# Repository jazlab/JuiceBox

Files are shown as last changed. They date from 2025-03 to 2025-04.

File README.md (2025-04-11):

# :beverage_box:JuiceBox: a liquid reward delivery system

JuiceBox is a liquid reward delivery system designed for animal training and experiments. The system consists of:

1. A control box, which:
    - allows for valve control via computer (auto) and manual inputs,
    - features timed-draining for safe and convenient cleaning, and
    - includes mounting holes for the valve and a tube holder.
2. A bottle holder, which:
    - securely holds the juice bottle in place,
    - allows for quick and easy bottle removal, and
    - includes a tube holder to keep your hands free.

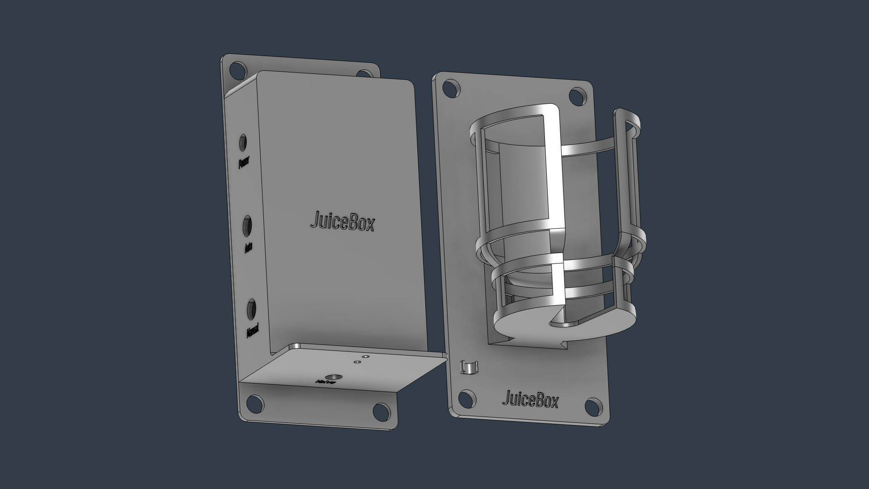
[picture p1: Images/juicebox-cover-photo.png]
Cover photo


## Table of Contents
- [Building & setting up your own JuiceBox](#building--setting-up-your-own-juicebox)
- [Using JuiceBox](#using-juicebox)
- [Circuit diagram](#circuit-diagram)
- [Latency test](#latency-test)
- [Contact](#contact)

## Building & setting up your own JuiceBox

### 0. Gather tools and supplies

The table below lists all the tools and supplies you’ll need to build a JuiceBox from scratch. If you already have a functioning control box, you’ll only need a 24V DC power cable, things listed in “Juice Bottle & Holder” and “Mounting,” and any relevant tools.

|  | **Name** | **Qty** | **Purpose & Specifications** |
| --- | --- | --- | --- |
| **Circuit Board** | PCB board | 1 | Custom files provided in this repository. See ordering instructions below. |
|  | 7805 voltage regulator | 1 | Can be pre-assembled on the PCB board (see PCB ordering instruction below). [Example product](https://www.amazon.com/ALLECIN-L7805-Regulator-Positive-Regulators/dp/B0CBKCDT4H/ref=sr_1_4?crid=2WCJKAQUHKRN7&dib=eyJ2IjoiMSJ9.yJzEi34CZ1WRm1_J6qxU1pyW9wghQLtg6IbF4fboZbTi889ok1h4hG9QhPJFAEpCzUIHdzyGpYp6OKTvsvIaCrYhlPovNcXIZuAi9Dkfmnm6QhzktdkW-ZoMuQcdPGAh4T31KEgbjpQAathV_9ffThyl1RSwhNaUL8IgItWbd8ZooAMghe03Zn5gxsPbM6_Zx74NqrIcUzpZuqI0Oic3-y2wBG06QpNkweJO2UbEySM.Bm0LgsJNeZJxWlu8izlvLKQT0AeiNju88KjW7ySMW00&dib_tag=se&keywords=7805%2BVoltage%2BRegulator&qid=1731457314&sprefix=tip122%2Bbipolar%2B%2Bbjt%2B%2Btransistor%2Bnpn%2B-%2Bdarlington%2B100v%2B5a%2B2w%2Bthrough%2Bhole%2Bto-220%2Caps%2C106&sr=8-4&th=1) |
|  | TIP122 bipolar transistor NPN | 1 | Can be pre-assembled on the PCB board (see PCB ordering instruction below). [Example product](https://www.amazon.com/ALLECIN-TIP122-Darlington-Transistor-Transistors/dp/B0CBKHTF9Z/ref=sr_1_3?crid=NHRWZAHM1KV9&dib=eyJ2IjoiMSJ9.h3c-xIy3MyTNjNTX3uCVtWWhdCAKbOBndhBnrGHPSWJUYxQc2KRioEiGCYQBQcaRg4totEood89ma_FmvDkk3stY6_0givGyjF8UUVD97Pjm6ek0hKZ99DP62D-fp6lwyGHInEgTdVrOV93C7CnteNRl2_INSGFWc2m_ZW1P5-Mf1aypLYuwvF-b5je-ar5emGewDr7abdsp8Gmo1LIBanKPAjnUqUAsEpXOZKP4wJY.HsZmLjGl8ASvvx4FFpKWcOrIbTktyNr3QxbMoi2U8qs&dib_tag=se&keywords=TIP122%2BBipolar%2B(BJT)%2BTransistor%2BNPN%2B-%2BDarlington%2B100V%2B5A%2B2W%2BThrough%2BHole%2BTO-220&qid=1731457071&sprefix=tip122%2Bbipolar%2Bbjt%2Btransistor%2Bnpn%2B-%2Bdarlington%2B100v%2B5a%2B2w%2Bthrough%2Bhole%2Bto-220%2Caps%2C143&sr=8-3&th=1) |
|  | 1N4007 diode | 1 | Can be pre-assembled on the PCB board (see PCB ordering instruction below). [Example product](https://www.amazon.com/Gratux-1N4007-Junction-Standard-Rectifier/dp/B094ZL2D1D/ref=sr_1_4?crid=29Z6BU8XTI3JY&dib=eyJ2IjoiMSJ9.WTasZ6bLzkfYGOf6drxvnZU7VKBncva7np3YBChdvqWEyGsSoZxENb71OisgmP76NQ6-iQRkSsRHx1cV--fE_tIpnlRFOTjXD_QRiwxDvn6MgZBxy8WwaKEAgNIzW0JRIEcasM6-UWq7BOQEt5mdzwl5qla0ZNYpBozhZPNFt3JJGcCcfrYQu3qfFrHECAcZtwPQHVAonbcnxsZtaFPbfQRD0-Xv3EkaQutWgrXfOYA.Lck7D6KoyzXsiKviougeUGX83vtRvIIcHRxwnV-D8js&dib_tag=se&keywords=Diode+1N4007&qid=1731457386&sprefix=diode+1n4007%2Caps%2C363&sr=8-4) |
|  | 10kΩ resistor | 1 | Can be pre-assembled on the PCB board (see PCB ordering instruction below). [Example product](https://www.amazon.com/EDGELEC-Resistor-Tolerance-Multiple-Resistance/dp/B07QJB31M7/ref=sr_1_4?crid=3W0PGIGRATIF3&dib=eyJ2IjoiMSJ9.6LwS_eL7GUDzrQTHCbHoUrXbUU6GcLf0Oh8KSANGZZdL6R_ioPvyKDDQzauwyocWAuH3uBKmSpWpA_eLq0MN4xKo8bmwQI0SGAySut8kUdZWewfVtrmSt_84dPwnOGJruGBS2MqxdSw4U9RSSM5YlSGHeTFUmjxPcRQ4s1W2re7aTogJlQVbuV81ZufTKkF5W34owsloKbJ7khKqYiVpWbWT21vB-TlA58s44IKvpGs.H3vq5bNiRlspgB_dFPIU1vL0NQbb9xow7vAFLmVgaQk&dib_tag=se&keywords=10k%2Bohm%2Bresistor&qid=1731457561&sprefix=10k%2Bohm%2Bresistor%2Caps%2C132&sr=8-4&th=1) |
|  | 1kΩ resistor | 1 | Can be pre-assembled on the PCB board (see PCB ordering instruction below). [Example product](https://www.amazon.com/EDGELEC-Resistor-Tolerance-Multiple-Resistance/dp/B07QG1V4YL/ref=sr_1_4?crid=9NGTKX7GOGT5&dib=eyJ2IjoiMSJ9.sjCrXtEr0PMGKZXQLPwE43Cm6Wuj_WtcdUxQqil3rZKYmxsW4Hdgn-4ivHmgXhPIXi8GvcwZnD0TmNpFv3DZBSPKdfVEAqTo1g4hwDk6zHdOYBZBGA2zZd_AWqRBViXud4u0CQg8fOSFjpMFEOFSoZWOGK9OgKwov7B3yMGC6-D05ZK2Zr9Qa5IDsuLBAQbISwKExnlai8jGw5q-4knqfeUevEgE2gigcbWQJIJjhKA.NTQfoTQ23CI5UKpTUx2ALHZFxTXFkuewyLlWkqgpxLI&dib_tag=se&keywords=1k%2Bohm%2Bresistor&qid=1731457618&sprefix=1k%2Bohm%2Bresistor%2Caps%2C80&sr=8-4&th=1) |
|  | Timer relay module | 1 | For timed-draining. Should allow at least ~3 minutes of circuit activation. [Example product](https://www.amazon.com/Coliao-Relay-Programmable-Delay-Trigger/dp/B0C6PRP3SD) |
| **Control Box** | JuiceBox control box (2 parts) | 1 | Custom STL & STEP files provided in this repository. See printing instructions below. |
|  | DC power female jack | 2 | For connecting the power cable and the solenoid valve. Mounting hole size: 8mm. [Example product](https://www.amazon.com/Antrader-24pcs-Female-Socket-Connector/dp/B07CTCLKPP/ref=sr_1_7?crid=27E3ZA791MXGN&dib=eyJ2IjoiMSJ9.G0qsGqVtqUh_MzpxbfzFVR_ahLdPyr4hm5xM-HFQozcQ5FGNJ7Iyi5FGI7u5KXu5W25WerjXk0ZjkQ8R0gSKAx1BV9jjVTAYTzSGYGEux7TBotKe2JQzrNXtaOEtW2cOmYkwMoPraN8CAxFcpwvbK-3pJwrMqFeP2NRD6toxj3u8EaMovjeXwCsVGCpApjfzVGqZDhnmzhvnn3IPJoBPNvLd1aDCAD4Vz_Uqx7f93CkfIkFt3QiTttKnCcPzlMG0IDJO-pBR2kG0uLUeVv6Mg0gIZyGM6ZeaqnZ8DYtWlvw.2gLL3oBBm8bbSFGmCYeUkpFK7pTFvhp3nbEr3FNgCYs&dib_tag=se&keywords=24V+DC+Power+Jack+Female&qid=1731459468&s=industrial&sprefix=24v+dc+power+jack+female%2Cindustrial%2C69&sr=1-7) |
|  | BNC female connector | 2 | For connecting auto and manual inputs. Mounting hole size: 10mm. [Example product](https://www.amazon.com/Hxchen-Female-Bulkhead-Insulated-Connector/dp/B07V1SWM9J/ref=sr_1_1?crid=2NG5997LXJS1G&dib=eyJ2IjoiMSJ9.DqvluEvvbyZoupcrHrtUDo3ia0fTd9TcnjKIpQs7Jn63A2n4Am_if-ZBLvsjAhCQYrIagbD-fAVcue69FS0aDIaCi_EUqk4EHWzI5Yt2JZVUx9ZoQf6Uv7P-RLAy-GClVXxCdszSs-HQpH8CSDyM4YRiuxBnrUIK3dx7wMRbkmSmlHqoBtnVcueZfO16186F1lBa_nBr8OiG9a2JRSZlZl5nIpSlt9D3z_ZcymH-dHvhaMIySPkN9TEmdUmSGH3hid4kgAeg6MbhqojkSE-hGjbZxnLG2N6wINCAV6vGpAk.bJCI6rmy8P2Kts4S21CpPxp6Qc3F2SUEnrVzPqtmF4Q&dib_tag=se&keywords=BNC+Female+Jack+Bulkhead+Solder+Panel+Mount+Insulated+Coax+Rf+Connector&qid=1731458227&s=electronics&sprefix=bnc+female+jack+bulkhead+solder+panel+mount+insulated+coax+rf+connector%2Celectronics%2C259&sr=1-1) |
|  | Momentary push button with LED light | 1 | For timed-draining and drain signal light. Mounting hole size: 12mm. [Example product](https://www.amazon.com/dp/B0C38V5TY5?ref=fed_asin_title&th=1) |
|  | DC power male plug | 1 | To be soldered onto the solenoid valve. [Example product](https://www.amazon.com/Fancasee-Replacement-Solder-Connector-Adapter/dp/B07Y8M8TWM/ref=sr_1_1_sspa?crid=2RDTN4C3PBLUR&dib=eyJ2IjoiMSJ9.PJr6EG-Jalyz612j4p3UJfSf8D1HD5KMjlq1QGLVs5FQDX76ZjZ8GPVaFXS35Tge_L_9MvSrKagtzCC2VnKADLzaXi6-iyjtz7NY_M1UUe9jsjRuFaDTv1GRJWAFiIxVILuUI4c0PDGBltAWYaeeVZOeiL_uGoXBioNkdi3eBtMDhciiCP9jnhKzUzC90jtno93tNryqJipnfFiftSEhO33Ajm5h9ZZf6-KV40YusYY.TjM1M5agFEvbo74nm8Ixgfc3lenq8qVDp9dKAW9R8qM&dib_tag=se&keywords=male+power+jack+solder&qid=1731463868&sprefix=male+power+jack+solde%2Caps%2C153&sr=8-1-spons&sp_csd=d2lkZ2V0TmFtZT1zcF9hdGY&psc=1#customerReviews) |
|  | Solenoid valve | 1 | For dispensing liquid reward. [003-0257-900 Parker Hannifin](https://ph.parker.com/us/en/product/series-3-miniature-inert-liquid-valve/003-0257-900) |
|  | 4-40 screws | 14 | For mounting the PCB boards and closing the lid of the control box. 4-40, 0.25 inch long, Coarse (UNC). [Example product](https://www.mcmaster.com/90272A106/) |
|  | 24V DC power cable | 1 | Power input to the control box. [Example product](https://www.amazon.com/TKDY-110-240V-Soundbar-Diffuser-Humidifier/dp/B08F7DVY8G/ref=sr_1_1?crid=2XTC3WP66E4PS&dib=eyJ2IjoiMSJ9.1rwGyqucQMA0ikWW6m25nZlqNzJLzthmtLffw5Vmouw-WYvEX63Ih_JTnVeNnlVLTlo2rXA_iYsOXJBz0A9que0eISOFq83kk_4gZlfP7D4poAV-EiKVw8wKZBsFUrAL0xUFKfikXNYo0vFUbfz5J1l1bPNbfd9-bpqSDgJZKzuQbTj1Gq9k-nuf7STRpD2-Ve6v7EZgpyID-JCGcoVAhlfz7tqeRj5X5zDHWoiEo7g.mf3D35VGWo5KkCPKBrZ9MfFbitbzkuL6UN6FctduNGQ&dib_tag=se&keywords=24V+DC+power+cable&qid=1739488720&sprefix=24v+dc+power+cable%2Caps%2C95&sr=8-1) |
| **Juice Bottle & Holder** | JuiceBox bottle holder | 1 | Custom STL & STEP files provided in this repository. See printing instructions below. |
|  | Wash/squeeze bottle | 1 | For holding liquid reward. Roughly 500mL, 73mm diameter, 53mm closure. [Example product](https://www.amazon.com/gp/product/B000N478A8/ref=ppx_yo_dt_b_search_asin_title?ie=UTF8&psc=1) |
|  | Plastic tubing |  | For delivering liquid reward. Inner diameter: 1/8 inch, outer diameter: 1/4 inch. [Example product](https://www.mcmaster.com/5233K52/) |
| **Mounting** | Mounting screws (optional) | 8 | For mounting the control box and the bottle holder. The mounting holes on the control box and bottle holder are 9mm in diameter. |
|  | Mounting nuts (optional) | 8 | For mounting the control box and the bottle holder. Size: same as the mounting screws. |
|  | Velcro strips (optional) |  | For mounting the control box and the bottle holder |
| **Tools** | Soldering tools (soldering gun, solder, wires, wire stripper, etc.) |  | For making the control box circuit. |
|  | 4-40 taps | 2 | For tapping the holes on the control box. 1x taper tap + 1x bottoming tap. [Example product](https://www.amazon.com/MaxTool-THREAD-3-Piece-Bottom-HSN02W00R04/dp/B07J1MJJ6X?th=1) |
|  | Phillips-head screwdriver(s) | 1-2 | For screwing 4-40 and mounting screws. |
|  | Scissors/blade/saw |  | For cutting the squeeze bottle and tubing. |

> [!NOTE]
> **Instructions for ordering the PCB board:**
> - You can order the PCB board from [JLCPCB](https://jlcpcb.com/) (cheap and fast, highly recommend) or similar vendors of your choice. To do so, upload the Gerber files *(juicebox_gerber)* onto the vendor’s website. You can customize the board settings (e.g. color, thickness, materials, etc.) if you want to, but most likely you don’t need to change anything.
> - If you dislike soldering or want to save some time, you can also ask the vendor to pre-assemble some components (e.g. the voltage regulator, transistor, diode, and resistors) on the PCB board. To do so, add “PCB Assembly” to your order. Upload the Bill of Materials file *(juicebox_bom.csv)* and Component Placement List file *(juicebox_cpl.csv)* when prompted. Each vendor may have slightly different requirements for these two files. If you’re ordering from JLCPCB, you can use the files in this repository directly; otherwise, you may need to tweak the format. After the system processes these files, you can confirm the choice of materials and their positions on the board.

> [!NOTE]
> **Instructions for 3D printing:**
> - Material: There is no strict requirement for the printing material, but you should make sure it’s tappable and water-resistant. I used grey resin and it worked.
> - Resolution: I used 0.05mm and it worked well — there’s no need to go finer than that.
> - There is also a mirrored version of the control box where the locations of the ports and the drain button are flipped. You can decide which version to use depending how your space is set up.

### 1. Assemble the control box

1. Tap the 12 screw holes on the control box with 4-40 taps. For best result, tap each hole with a taper tap followed by a bottoming tap to make the threads reaches the bottom of the hole.

<p align="center">
  
</p>

2. Solder the following parts onto the PCB board (skip this step if your PCB board was pre-assembled):
    - 7805 voltage regulator
    - TIP122 transistor
    - 1N4007 diode
    - 10kΩ resistor
    - 1kΩ resistor

<p align="center">
  
</p>

3. Short the power and trigger GND pads on the relay module.

<p align="center">
  
</p>

4. Insert and secure wires (of appropriate length) into the following connectors on the relay module:
    - Power
    - GND
    - Trigger
    - COM
    - NO

<p align="center">
  
</p>

5. Secure the PCB board and the relay module inside the box with 4-40 screws. The relay module should be on the top, the PCB board on the bottom.

<p align="center">
  
</p>

6. Insert and secure all connectors in the corresponding holes:
    - 2x DC power female jacks: “Power” & “Valve”
    - 2x BNC female connectors: “Auto” & “Manual”
    - 1x push button: “Drain”

<p align="center">
  
</p>

7. Solder wires (of appropriate length) onto the following connectors (or, if the connector came with wires, cut and strip the wires to desired length):
    - 2x DC power female jacks
    - 2x BNC female connectors
    - 1x push button
8. Solder the other end of the wires onto the corresponding pads on the PCB board.
   - For the DC power jack, make sure to solder the positive pin to the “24V” pad and the ground pin to the “GND” pad. For the example product linked above, the longer pin is the ground pin.
    - For the "Auto" BNC, solder the signal (center) pin to the "Signal" pad and the ground (peripheral) pin to the "GND" pad.
    - If you are using a push button with LED, make sure to differentiate the wires for the button and the wires for the LED. The LED should have a positive and a negative end. If you are using a drain button without LED, simply short the two pads labelled “LED.”

<p align="center">
  
</p>

9.  Solder a DC power male plug to the solenoid valve wires.
    - The valve is symmetric, so it does not matter which wire gets connected to which end of the power plug.

<p align="center">
  
</p>

10. Set the desired drain duration and mode on the timer relay module:
    1. Connect the DC power cable to the box. The relay module should turn on.
    2. Long press “SET” for 3 seconds — the screen should show something like “P1.1.” Now, use the “UP” and “DOWN” buttons to navigate to P1.3. 
        - In mode P1.3, when the drain button is pressed, the relay turns on for a set duration (”OP period”) and then turns off. Re-triggering the module within the OP period will disconnect the relay and reset the module. This means if the drain button is pressed again before time is up, the draining will stop immediately and the timer resets.
    3. Once you are at the correct mode (P1.3), press “SET” again — the screen will flash “OP.” This is the maximum duration for which the valve will stay open. Press “STOP” until the screen shows “0.0.0.” — this shows the time in minutes. Other displays show time in seconds (e.g. 003. = 3 seconds). Use “UP” and “DOWN” to set the desired duration. For example, you can set the duration to 3 minutes (“0.0.3.”), which is typically enough for a full bottle of liquid to drain through.
    4. Once you’re done, long press “SET” for 3 seconds until the screen flashes “P1.3” and returns to the main display (“000”). Now the relay module is all set!
    5. It is suggested to turn the relay on sleep mode, so the display won’t stay on all the time. If you long press “STOP” for 2 seconds, the screen should flash either “O-d” (normal mode) or “C-P” (sleep mode) before returning to the main interface (“000”). This tells you which mode is currently active. Long press "STOP" again to toggle between these modes.
        - C-P (sleeping mode): If the relay is idle for 5 minutes, the display will turn off automatically. The program will keep working.
        - O-d (normal mode): Display is always on.
    6. If you are confused or want to learn more about the timer relay module, you can refer to [this webpage](https://www.hnhcart.com/blogs/learn/all-you-need-to-know-about-relay-timer-module?srsltid=AfmBOoqXPmc-TtnOS80VKcII2ll3dJII4rWGqjZ0Q2o4tU3tMAlhPOWK).
11. You’re almost there! Now let’s do a sanity test:
    1. Connect the the valve and any auto/manual inputs you may want to test.
    2. Press the drain button and/or sending auto/manual input signals. If the circuit is working properly, you should be able to hear/feel the valve opening and closing on command. The LED should also turn on and off when you’re using the drain button.
12. Now that your control box is working properly, close the lid with 4-40 screws.
13. Secure the solenoid valve onto the control box with 4-40 screws. You can mount the valve either upright or upside down.

<p align="center">
  
</p>

### 2. Mount the control box and bottle holder

The JuiceBox system can be mounted in various ways, depending on how your space is set up. Both the control box and the bottle holder have 9mm-diameter mounting holes on 4 corners, where you can use appropriate screws and nuts to mount them onto a thin wall or board. Alternatively, you may use adhesives, Velcro, etc.

### 3. Make the juice bottle and connect the juice tube

1. Cut the bottom of the squeeze bottle and trim to desired length. Cut or remove the tube inside the bottle, if any. 
2. Cut the tip of the squeeze bottle for optimal flow rate.
3. Place the bottle in the bottle holder.
4. Cut the plastic tubing to desired lengths. Connect one tube from the tip of the bottle to the valve, and another from the valve to wherever the liquid will be dispensed.

### Yay! Now you have your own JuiceBox :tada:

## Using JuiceBox

### Ways to control the valve

During animal training and experiments, you can control the valve by sending TTL signals (high = 5V) from an Arduino board to the “Auto” BNC port. You can code your own program to control the timing of reward delivery based on the animal's performance.

For manual reward delivery, such as during setup or preliminary training, you can either (1) use the drain button on the control box to toggle on/off, or (2) connect a push button ([example product](https://www.adinstruments.com/products/push-button-switches)) or foot pedal ([example product](https://onlytattoosupply.com/product/heavy-duty-tattoo-foot-switch-superman-footswitch-bnc-connector/)) to the “Manual" BNC port.

### Timed-draining

The “Drain” button allows you to drain or flush the juice bottle and tube after use. Its timed-draining feature prevents the valve from overheating during this process.

When the drain button is pressed, the valve will open for a set duration and then close automatically. If the button is pressed again before the time is up, the valve will be closed immediately. The LED light on the button turns on whenever the drain is on (this does not apply when the valve is opened by auto/manual inputs). You can change the maximum draining duration by configuring the relay module inside the control box (see relevant instructions above).

## Circuit diagram

In case you’re curious, here is the circuit diagram of the JuiceBox control box:

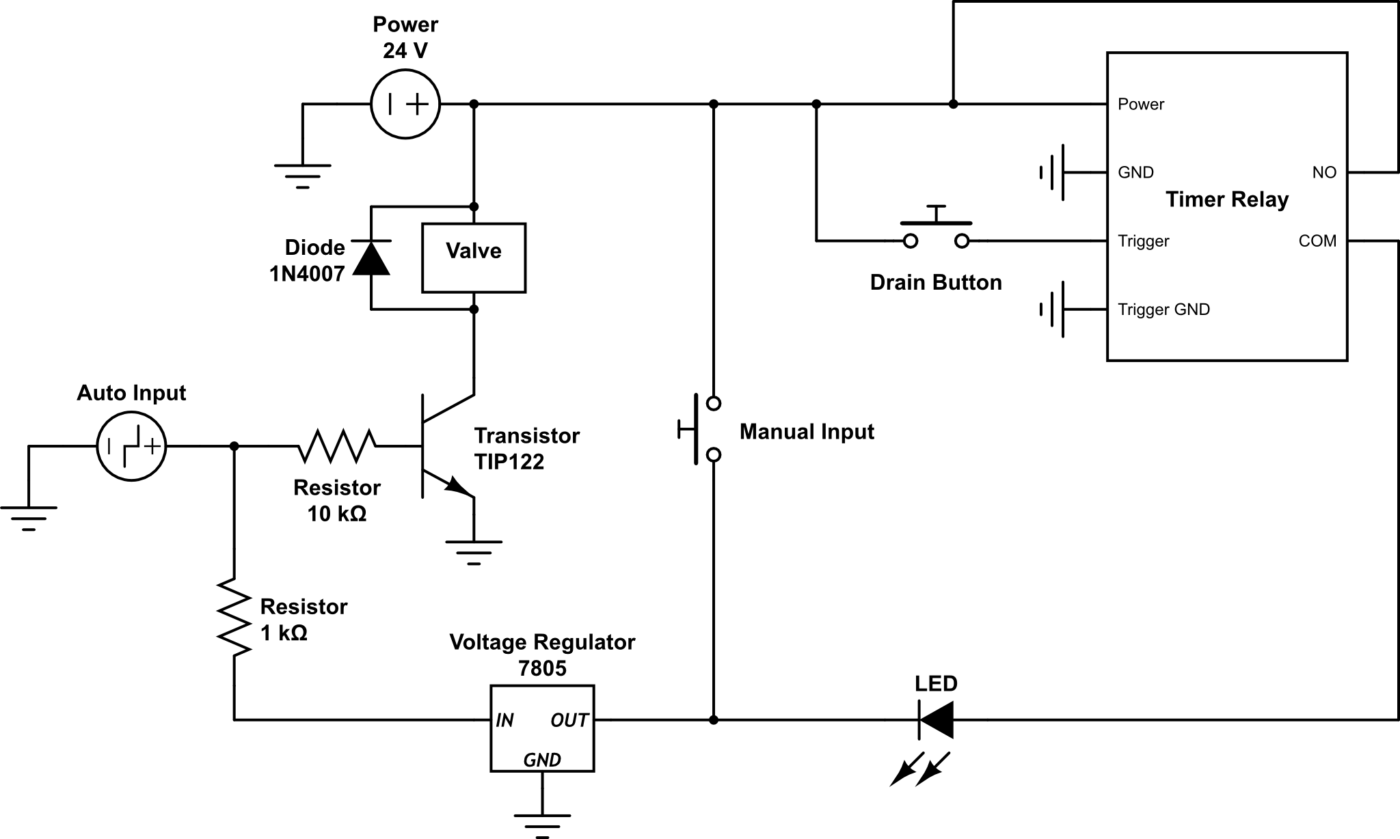
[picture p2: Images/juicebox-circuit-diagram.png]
JuiceBox circuit diagram


## Latency test

If you want to know the delay between TTL input signal to liquid reward delivery, you can perform a latency test with your JuiceBox system. One way to do this is to perform a “saline test.” Here is a schematic of the setup:

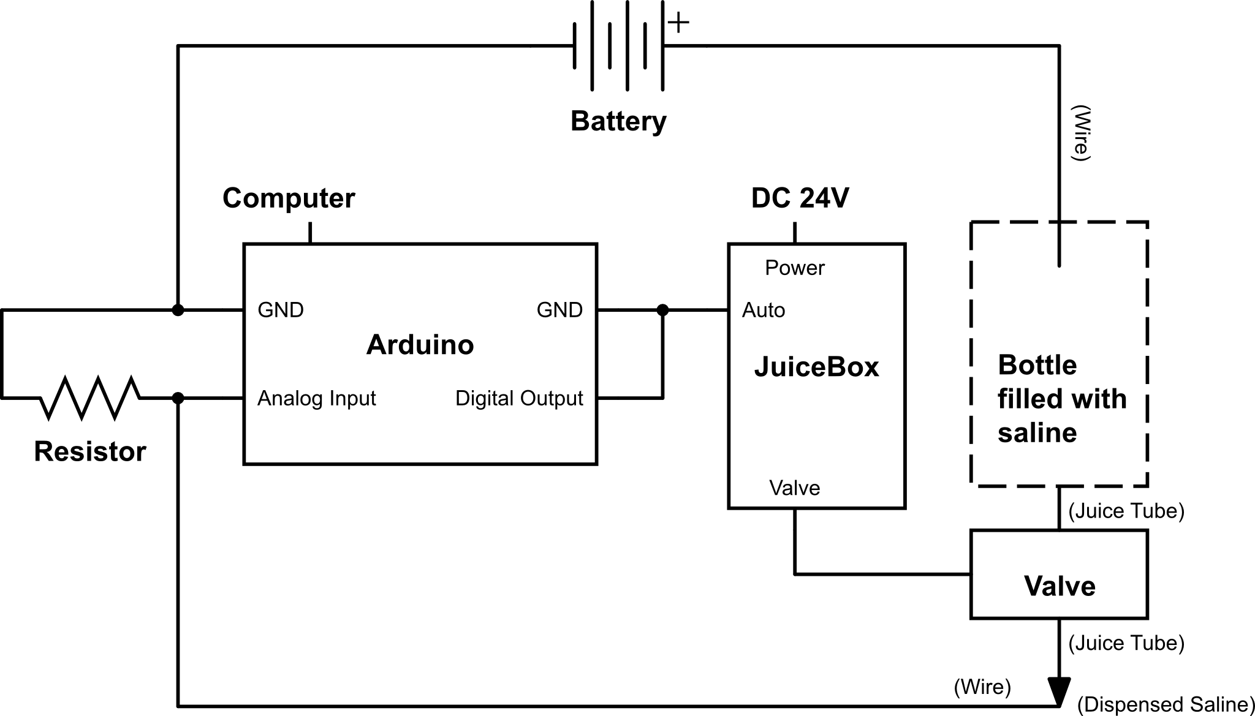
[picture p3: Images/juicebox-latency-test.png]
JuiceBox latency test schematic


Here is how to perform the test:

1. After setting up the JuiceBox, fill the juice bottle and tube with saline. 
2. Program an Arduino board that sends regular TTL pulses to the JuiceBox, monitors voltage changes from liquid delivery, and measures the time between the signal onset and voltage change (see code below).
3. Create a circuit as shown in the schematic above: one end of the wire is dipped in saline in the juice bottle, and the other end of the wire is at the tip of the juice tube. Whenever the valve opens in response to a TTL pulse, the saline dispensed from the tube immediately completes the circuit, creating a measurable voltage change.
4. Run the Arduino code for multiple trials and collect the latency data. Then you can calculate the mean latency and standard deviation of your JuiceBox system.
   
> [!TIP]
> Before running the test:
> - Make sure you have “primed” the saline such that it is just about to come out of the tube.
> - Make sure the end of the wire is a few millimeters into the tip of the juice tube (but not in constant contact with saline). Otherwise, the latency you measure will also include the time it takes for saline to travel to the wire.
> - It is also recommended to cycle the valve several times (at least 5 opens and closes) to prevent the its internal parts from getting stuck due to long periods of inactivity.

Here is how to program the Arduino board:

```arduino
// JuiceBox Latency Test
// - Turns solenoidPin HIGH for solenoidDuration
// - Measures elapsed time between solenoidPin activation and sensorPin voltage crossing a threashold 
// - Prints the elapsed time at the end of each trial
// - Repeat after testInterval

// Pin selections
const int solenoidPin = 2;     // Digital pin for solenoid control
const int sensorPin = A3;      // Analog input pin for voltage measurement

// Timing variables
unsigned long lastTestTime = 0;
const unsigned long testInterval = 5000;    // Repeat every 5 seconds
const unsigned long solenoidDuration = 200; // Open valve for 200 milliseconds

// Response time measurement variables
unsigned long startTime = 0;    // Time of solenoidPin activation
unsigned long responseTime = 0; // Time of voltage change
bool testRunning = false;
bool responseDetected = false;

// Voltage threshold
const float voltageThreshold = 0.1;  // 0.1 volts threshold
const float voltageConversion = 5.0 / 1023.0;  // For 5V reference and 10-bit ADC

void setup() {
  // Initialize serial communication
  Serial.begin(115200);  // Higher baud rate for faster serial communication
  
  // Set pin modes
  pinMode(solenoidPin, OUTPUT);
  digitalWrite(solenoidPin, LOW);  // Ensure valve is initially off
}

void loop() {
  unsigned long currentMillis = millis();
  // Start a new test every 5 seconds
  if ((currentMillis - lastTestTime >= testInterval) && !testRunning) {
    digitalWrite(solenoidPin, HIGH);
    startTime = micros();  // Start measuring time
    lastTestTime = currentMillis;
    testRunning = true;
    responseDetected = false;
  }
  
  // Check for voltage threshold crossing if test is running
  if (testRunning && !responseDetected) {
    float voltage = analogRead(sensorPin) * voltageConversion;
    if (voltage > voltageThreshold) {
      responseTime = micros() - startTime;  // Elapsed time
      responseDetected = true;
    }
  }
  
  // Turn off solenoid after 200ms
  if (testRunning && (currentMillis - lastTestTime >= solenoidDuration)) {
    digitalWrite(solenoidPin, LOW);
  }
  
  // End the test and prepare for the next one after a reasonable timeout
  if (testRunning && (currentMillis - lastTestTime >= 1000)) {
    // Print the elapsed time at the end of each trial
    if (responseDetected) {
      Serial.println(responseTime / 1000.0, 3);  // Convert to milliseconds with 3 decimal places
    } else {
      Serial.println("No response");
    }
    testRunning = false;  // End the current test
  }
}
```

## Contact

For inquiries and suggestions, feel free to contact Yuelai Feng at yuelai.f@outlook.com.

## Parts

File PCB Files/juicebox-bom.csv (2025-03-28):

Comment | Designator | Footprint | JCLPCB Part #
L7805 | U1 | TO-220D_STM | C111887
10kOhm | R1 | R_Axial_DIN0411_L9.9mm_D3.6mm_P15.24mm_Horizontal | C410695
TIP122 | Q1 | TO-220-3_Vertical | C16283
1kOhm | R2 | R_Axial_DIN0411_L9.9mm_D3.6mm_P15.24mm_Horizontal | C713997
1N4007 | D1 | D_DO-41_SOD81_P10.16mm_Horizontal | C19357

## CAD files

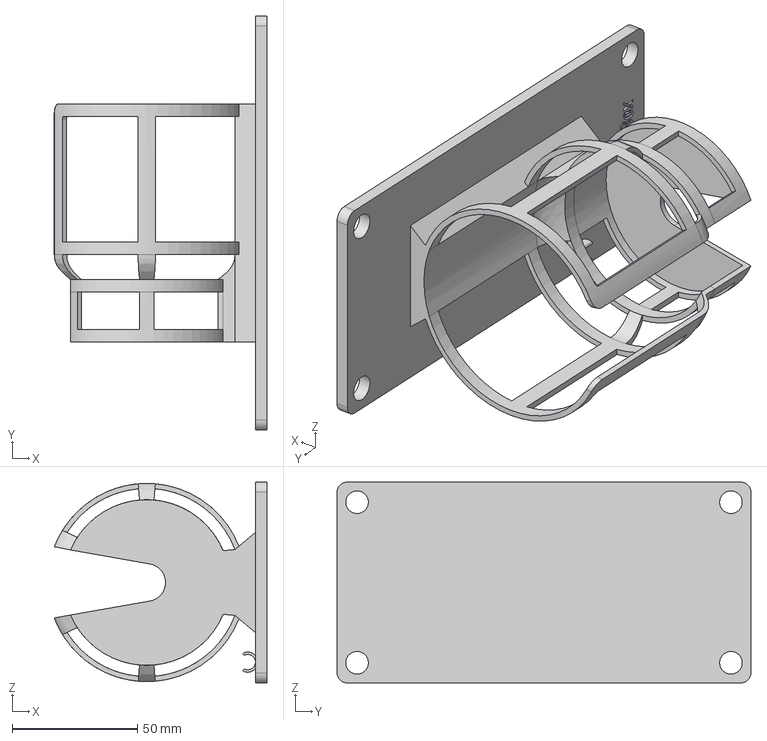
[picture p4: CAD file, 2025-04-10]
CAD Files/juicebox-bottle-holder.step
84.7 x 165.0 x 80.0 mm

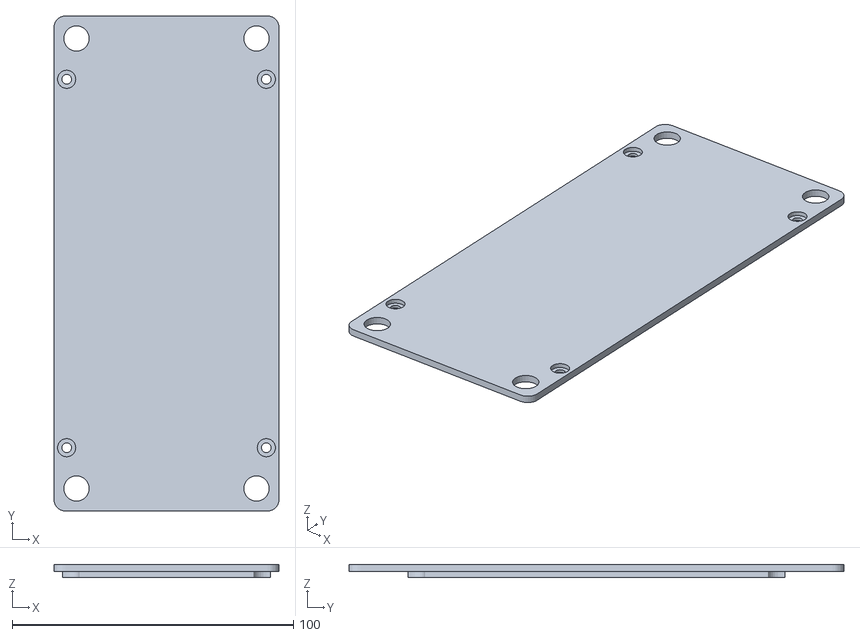
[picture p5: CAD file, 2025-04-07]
CAD Files/juicebox-control-box-lid.stl
80.0 x 176.0 x 4.50

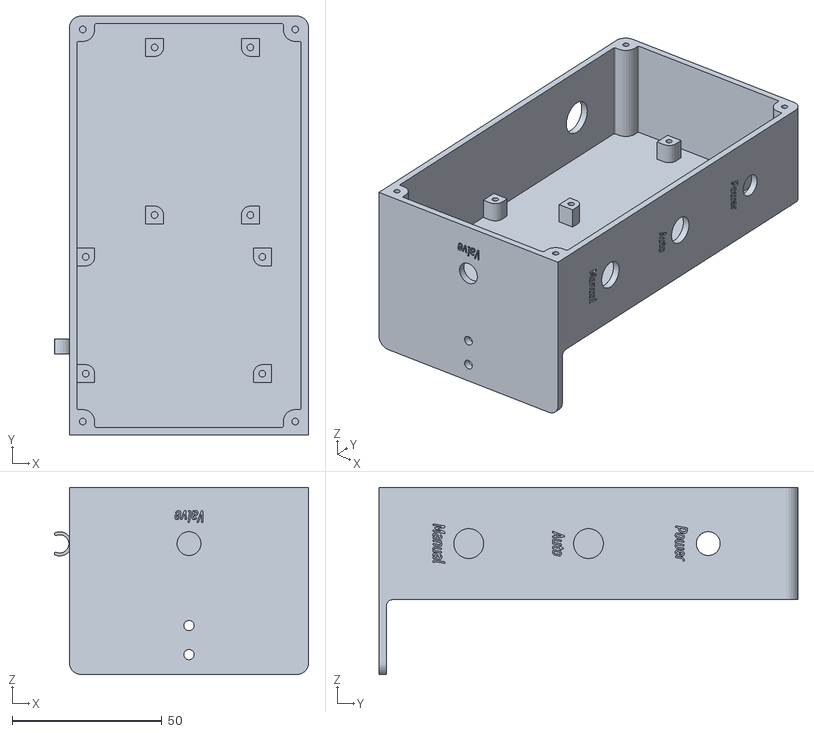
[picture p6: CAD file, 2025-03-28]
CAD Files/juicebox-control-box.stl
85.0 x 140.0 x 62.5

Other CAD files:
CAD Files/juicebox-control-box-mirrored.stl
CAD Files/juicebox-bottle-holder.stl

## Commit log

2025-03-27 added circuit diagrams
2025-03-28 added pcb and stl files
    [juicebox-bom.csv, juicebox-bottle-holder.stl, juicebox-control-box-lid.stl, juicebox-control-box-mirrored.stl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]
2025-04-01 added STEP files
    [juicebox-bottle-holder.step, juicebox-bottle-holder.stl, juicebox-control-box-lid.stl, juicebox-control-box-mirrored.stl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]
2025-04-07 minor adjustments to the CAD files
    [juicebox-control-box-lid.stl]
2025-04-10 minor adjustments to the CAD model
    [juicebox-bottle-holder.step, juicebox-bottle-holder.stl]
2025-04-10 updated pcb files
